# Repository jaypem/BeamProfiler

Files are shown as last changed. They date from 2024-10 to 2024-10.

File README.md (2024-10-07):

# BeamProfiler pd©

The BeamProfiler pd1© allows to measure laser beams with diameters up to 4 mm. It is controlled by a Raspberry Pi, a small single-board computer with an adapted 7” touch display.

| Camera parameter           | Laser beam                | BeamProfiler results              |
| -------------------------- | ------------------------- | --------------------------------- |
| Sensor Size: 5,7 x 4,28 mm | Beam diameter: up to 4 mm | Beam diameter $ \frac{1}{e^2} $ |
| Pixel: 2592 x 1944         | Wavelength: 350 – 950 nm | Width and height                  |
| Pixel Size: 2,2 x 2,2 µm  |                           | Image with scale                  |

For more information see also: `BeamProfiler-pd1_manual.pdf`

©Dirk Müller, JanPhilipp Praetorius

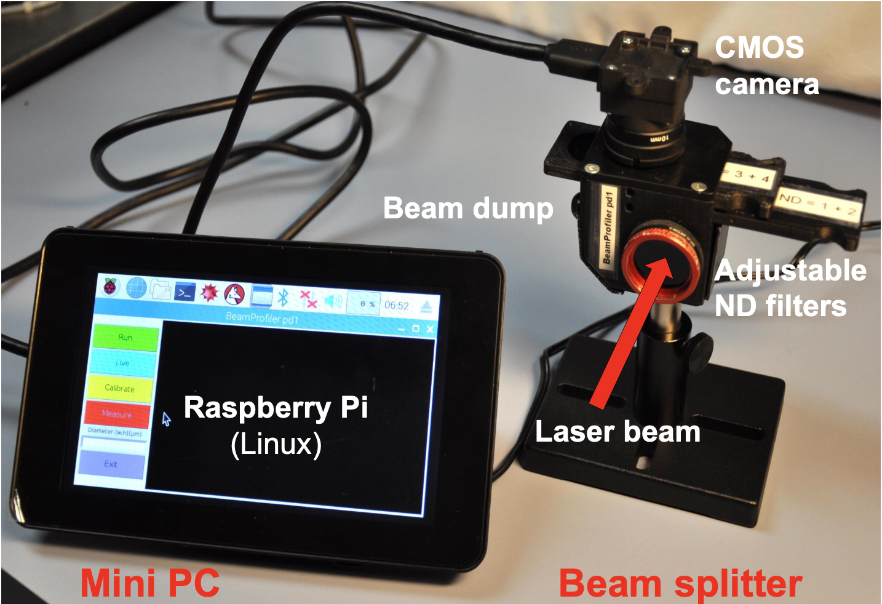
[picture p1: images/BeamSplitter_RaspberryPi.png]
BeamSplitter_RaspberryPi

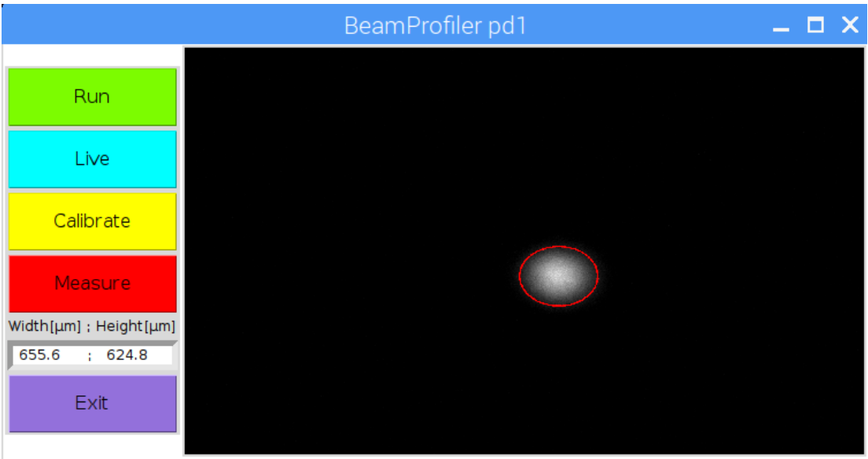
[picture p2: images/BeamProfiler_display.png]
BeamProfiler_display


## Assembly of the Raspberri Pi

### Install heat sinks one the Pi

[raspberrytips](https://raspberrytips.com/install-heat-sinks-raspberry-pi/)

### Setting up your Raspberry Pi

[https://projects.raspberrypi.org/en/projects/raspberry-pi-setting-up](https://projects.raspberrypi.org/en/projects/raspberry-pi-setting-up)

1. insert SD-card
2. connect the mouse to a USB-port
3. connect a keyboard to a USB-port
4. connect a screen via HDMI
5. connect power supply to micro-USB(the Pi starts to boot)

### Finish Setup

6. select corresponding settings

## Installation

### Install miniconda

run as bash command:

```bash
wget http://repo.continuum.io/miniconda/Miniconda-3.16.0-Linux-armv7l.sh
```

### Install python3 with

corresponding libraries on the Pi

7. [OpenCV]([https://tutorials-raspberrypi.de/opencv-auf-dem-raspberry-pi-installieren/](https://tutorials-raspberrypi.de/opencv-auf-dem-raspberry-pi-installieren/))

[fhttps://www.alatortsev.com/2018/09/05/installing-opencv-3-4-3-on-raspberry-pi-3-b/](https://www.alatortsev.com/2018/09/05/installing-opencv-3-4-3-on-raspberry-pi-3-b/)

OR

```bash
sudo apt install python3-opencv
```

Access via
ssh: [https://www.raspberrypi.org/documentation/remote-access/ssh/](https://www.raspberrypi.org/documentation/remote-access/ssh/)

8. install matplotlib

```bash
sudo pip3 install matplotlib
```

9. if numpy must be updated

```bash
sudo pip3 install –upgrade numpy
```

10. install PIL.ImageTk

```bash
sudo apt-get install python3-pil.imagetk
```

11. follow installation instruction for camera-library: [https://github.com/basler/pypylon](https://github.com/basler/pypylon)

11.1     download pylon-software for OperatingSystem: *ARM-32-bit:*

https://github.com/Basler/pypylon/releases:

install corresponding lib :

for python 3.5 install [pypylon-1.3.1-cp35-cp35m-linux_armv7l.whl](https://github.com/basler/pypylon/releases/download/1.3.1/pypylon-1.3.1-cp35-cp35m-linux_armv7l.whl)

```bash
pip3 install pypylon-1.3.1-cp35-cp35m-linux_armv7l.whl
```

11.2 To
commit permission for executing the shell script by double click go to desktop and type:

```bash
chmod u+x BeamProfiler.sh
```

## Connect Pi with Touchscreen

12. Remove screws of controller board at the backside of the display, put Pi on the appropriate screw socket and mount the Pi with the screws
13. Connect the cables from the controller board with the Pi as shown in the following link:

[https://maker-tutorials.com/raspberry-pi-touchscreen-installieren-und-anschliessen-tipps-tricks/](https://maker-tutorials.com/raspberry-pi-touchscreen-installieren-und-anschliessen-tipps-tricks/)

14. Start the Pi and if necessary rotate the display with the following command:

```bash
sudo nano / boot /config.txt
```

and add the following line on the top of the file:

`„lcd_rotate=2“`

15. Save the file and test the shell script **„BeamProfiler.sh“** on the Desktop

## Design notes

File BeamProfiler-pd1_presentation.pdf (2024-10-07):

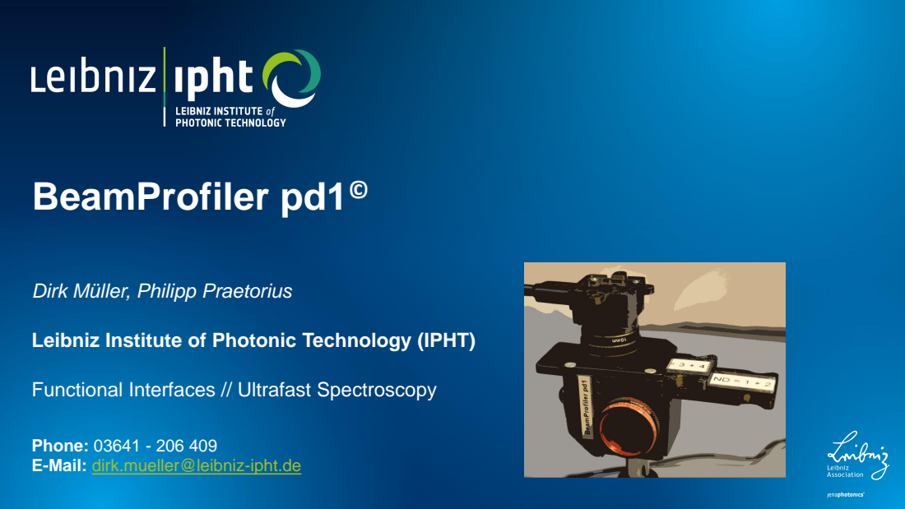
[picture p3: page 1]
BeamProfiler pd1©

Dirk Müller, Philipp Praetorius

Leibniz Institute of Photonic Technology (IPHT)

Functional Interfaces // Ultrafast Spectroscopy

Phone: 03641 - 206 409
E-Mail: dirk.mueller@leibniz-ipht.de

## Components of the BeamProfiler pd1©

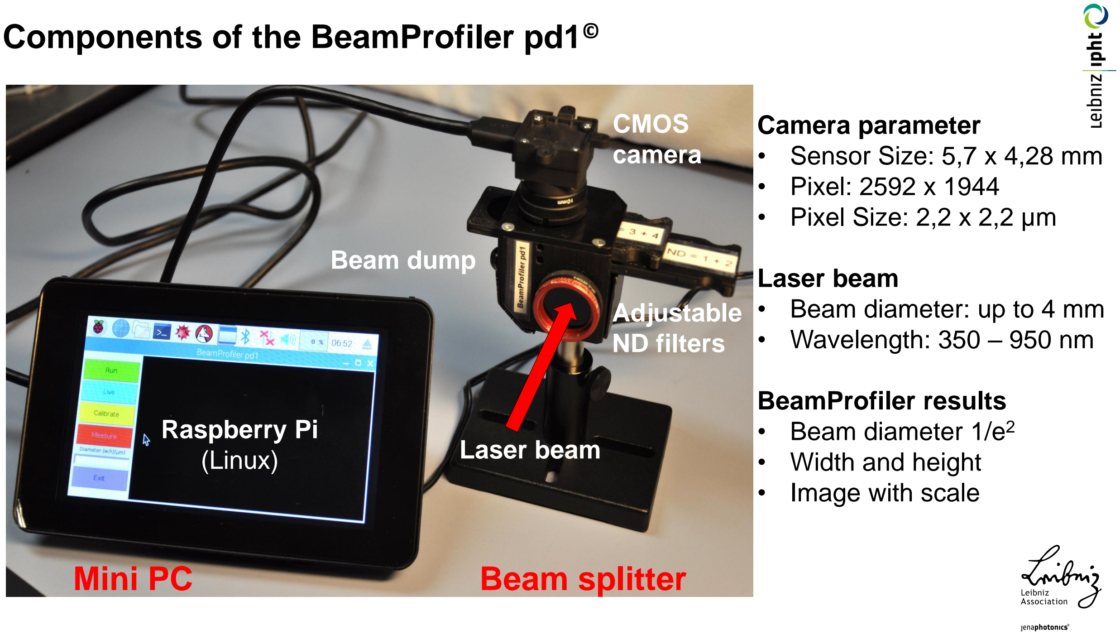
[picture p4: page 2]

CMOS
camera

Raspberry Pi
(Linux)

Beam dump

Laser beam

Adjustable
ND filters
Mini PC | Beam splitter

Camera parameter
- Sensor Size: 5,7 x 4,28 mm
- Pixel: 2592 x 1944
- Pixel Size: 2,2 x 2,2 µm

Laser beam
- Beam diameter: up to 4 mm
- Wavelength: 350 – 950 nm

BeamProfiler results
- Beam diameter 1/e

2
- Width and height
- Image with scale

## Setup of the BeamProfiler pd1©

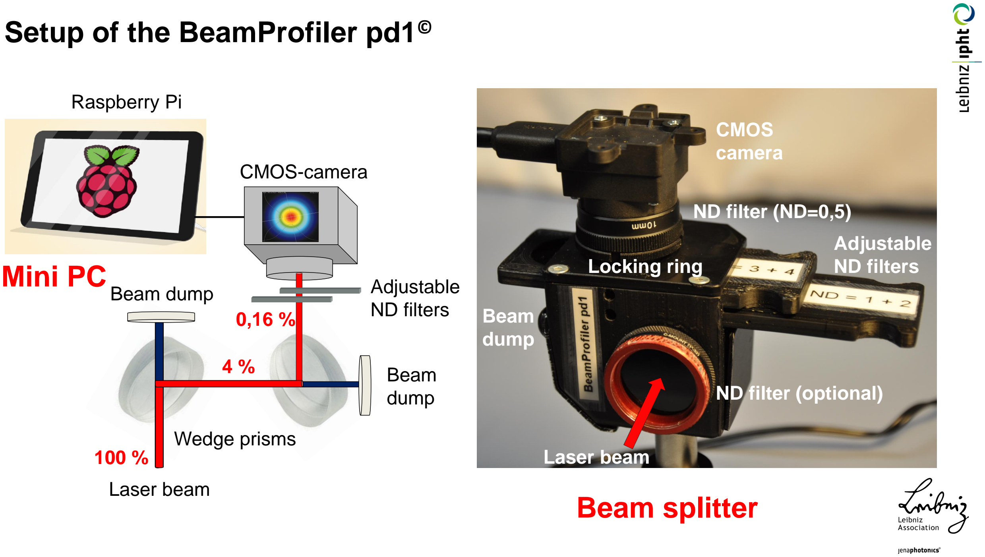
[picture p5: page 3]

CMOS-camera

Raspberry Pi

Adjustable
ND filters

Wedge prisms

Beam
dump

Beam dump

Laser beam

CMOS
camera

Beam
dump

Laser beam

Adjustable
ND filters

ND filter (ND=0,5)

Locking ring

ND filter (optional)

## Beam splitter

## Mini PC

100 %

4 %

0,16 %

## Adjustment of the BeamProfiler pd1©

Avoiding a damage of eyes and sensor
- Use the laser with the lowest power.
- Attenuate the laser power by external reducers (i.e. neutral density filter wheel).

Adjustment of the BeamProfiler pd1©
- Position the beam splitter at the right position. Consider the distance of about 88 mm from entrance to the sensor.
- Adjust the laser through the beam splitter primarily without the camera to find the weak signal behind the wedges.
- Turn off the camera together with the ND filter very carefully from the beam splitter.
- Put a white card or a diffusion disk on the exit of the beam splitter and adjust carefully the laser to the exit of the beam splitter. Pay attention to
the laser safety!
- Turn on the camera after adjusting the laser into

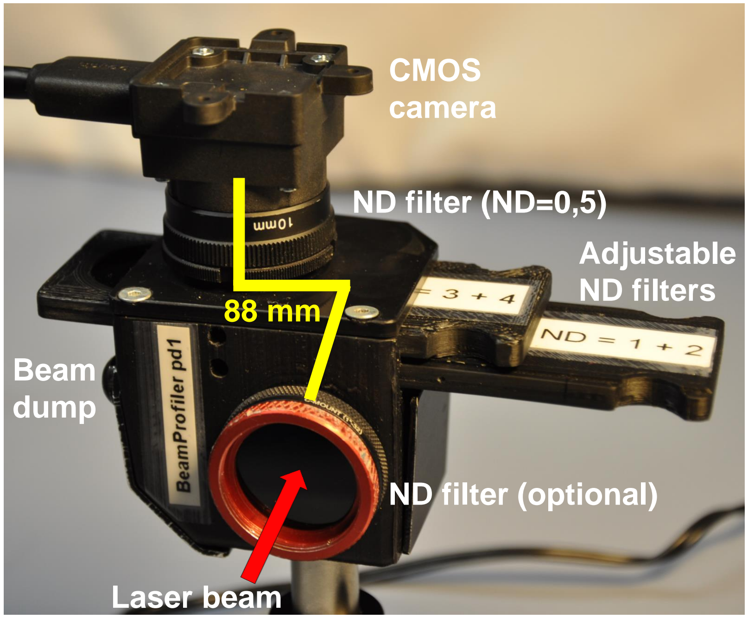
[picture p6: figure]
CMOS camera; Beam dump; Laser beam; Adjustable ND filters; ND filter (ND=0,5); ND filter (optional)

the center of the exit of the beam splitter. | Beam splitter

## Changing the direction of the BeamProfiler

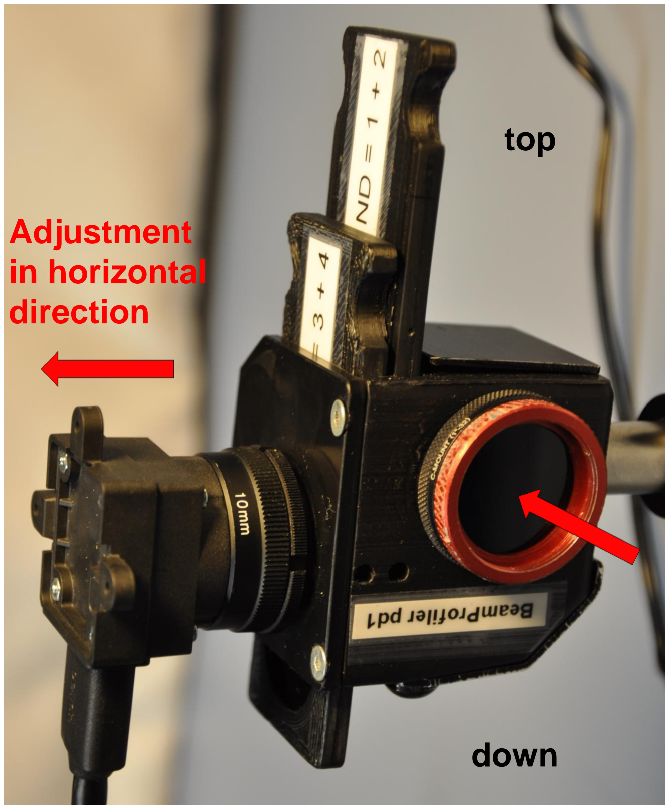
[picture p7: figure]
top; down; Adjustment in horizontal direction

## Operation of the BeamProfiler pd1©

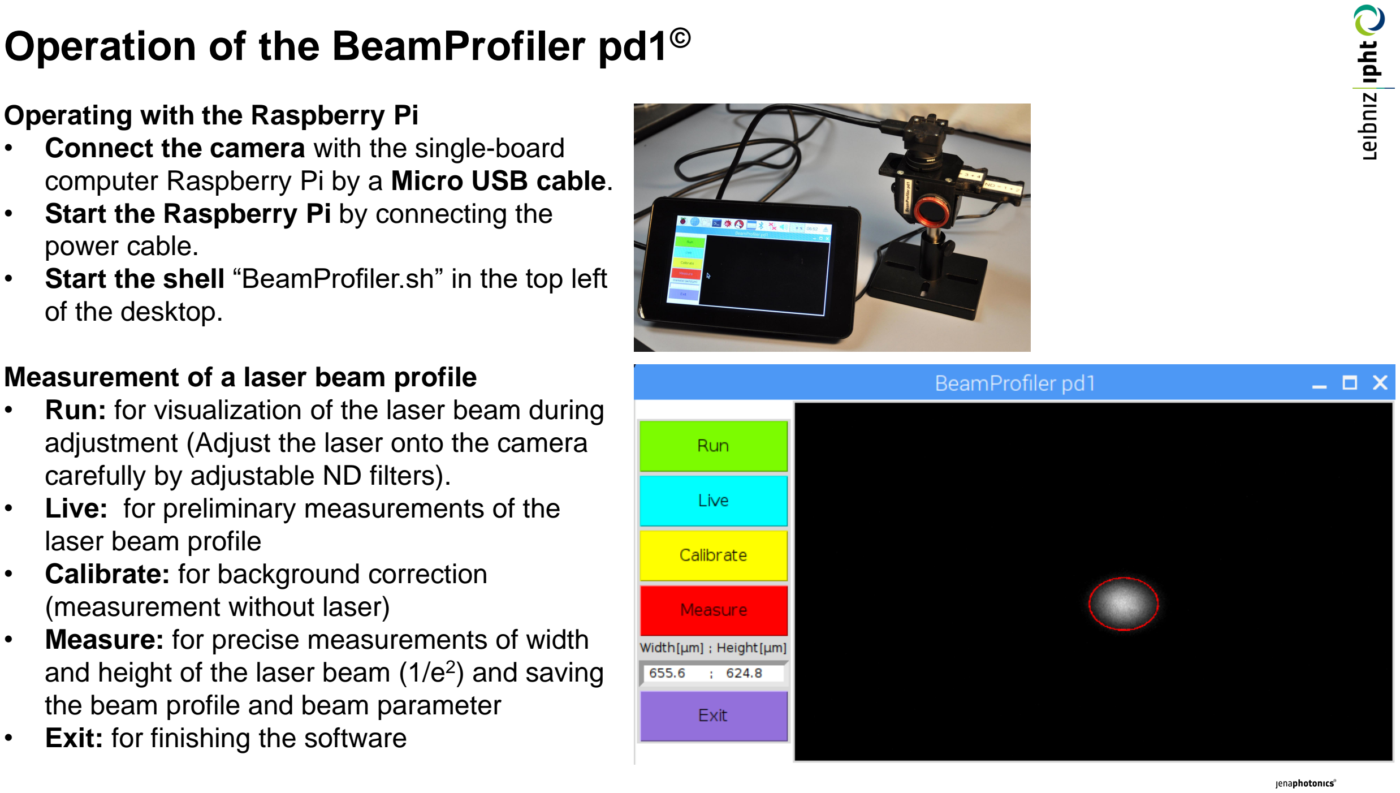
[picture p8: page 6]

Operating with the Raspberry Pi
- Connect the camera with the single-board computer Raspberry Pi by a Micro USB cable.
- Start the Raspberry Pi by connecting the power cable.
- Start the shell “BeamProfiler.sh” in the top left of the desktop.

Measurement of a laser beam profile
- Run: for visualization of the laser beam during adjustment (Adjust the laser onto the camera carefully by adjustable ND filters).
- Live: for preliminary measurements of the laser beam profile
- Calibrate: for background correction (measurement without laser)
- Measure: for precise measurements of width and height of the laser beam (1/e²
) and saving
the beam profile and beam parameter
- Exit: for finishing the software

## Output of the image and the measurement result

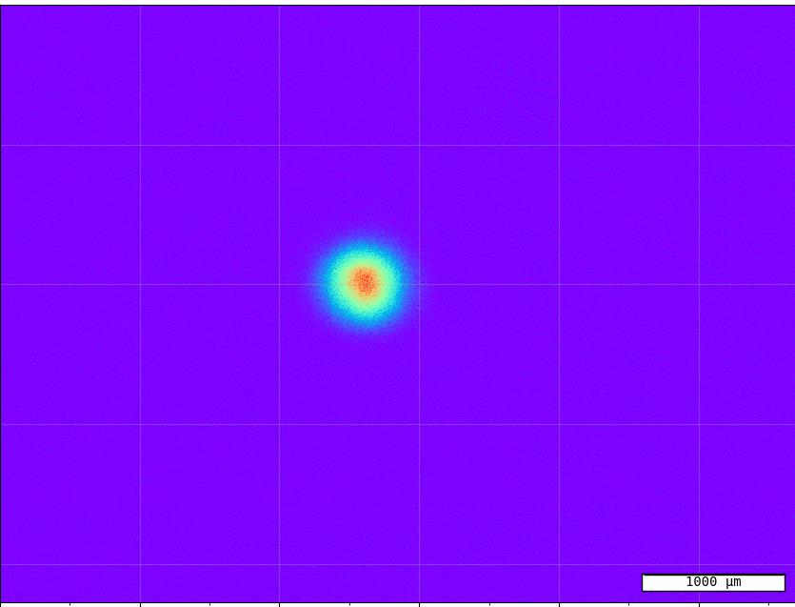
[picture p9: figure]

Beam paramter
- Beam diameter 1/e

2
- Width and height in µm

## Directory structure of the Raspberry Pi

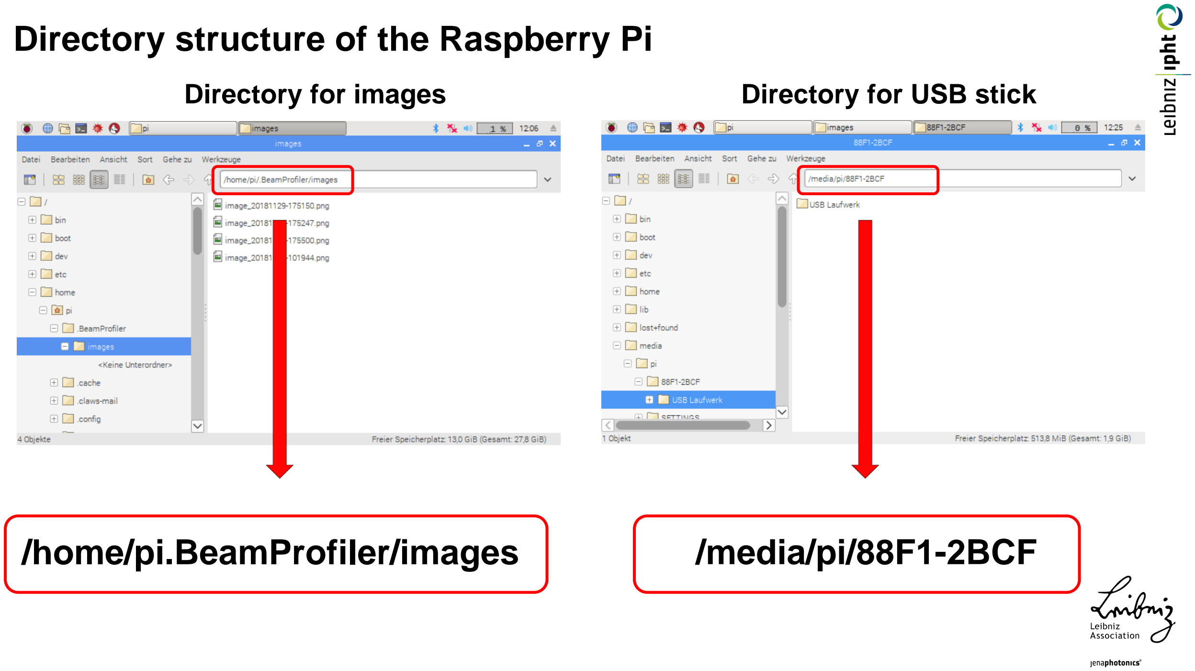
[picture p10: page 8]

Directory for images | Directory for USB stick
/home/pi.BeamProfiler/images | /media/pi/88F1-2BCF

## Examples: beam profile of a laser pointer

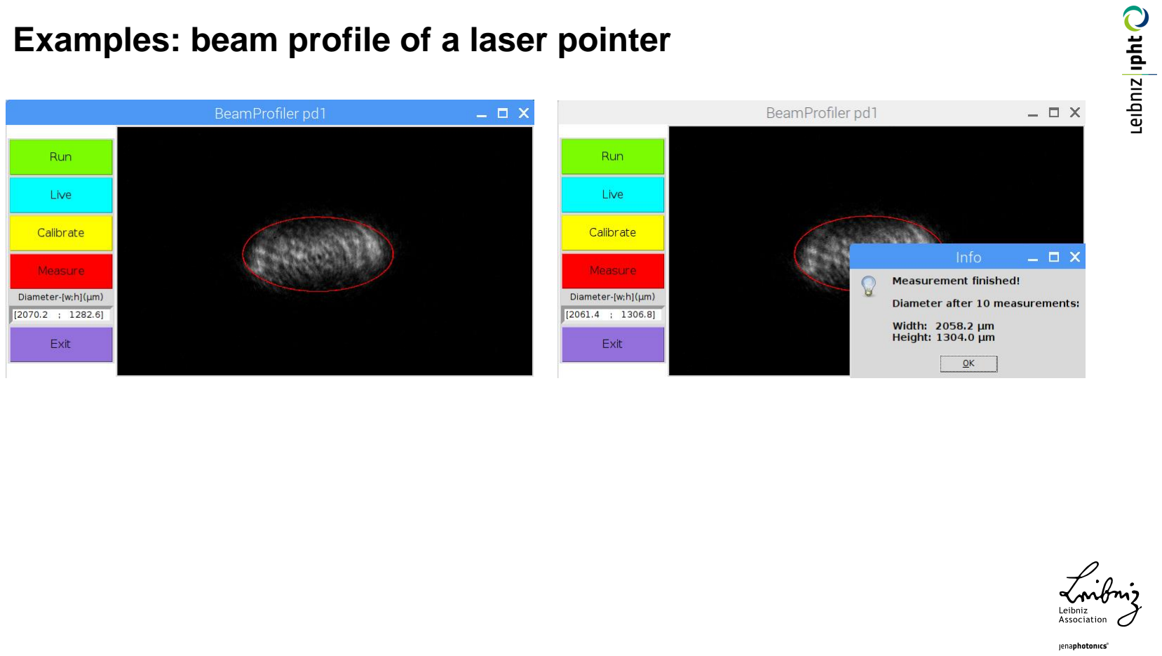
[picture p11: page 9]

## Examples: beam profile of the Tsunami laser (S21, streak camera)

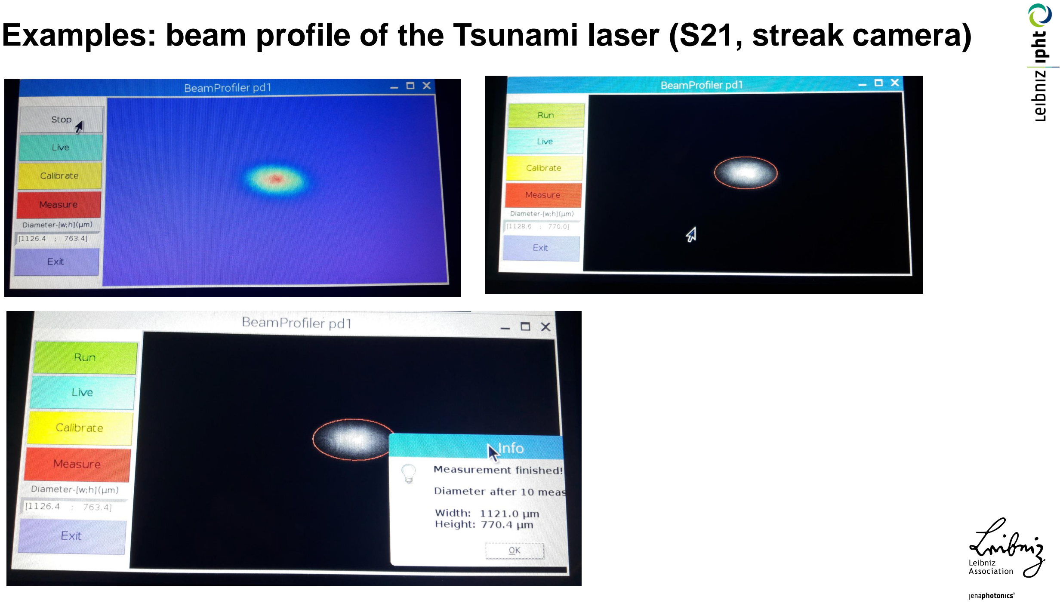
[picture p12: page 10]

## Examples: beam profile of the Legend (191.1, TA)

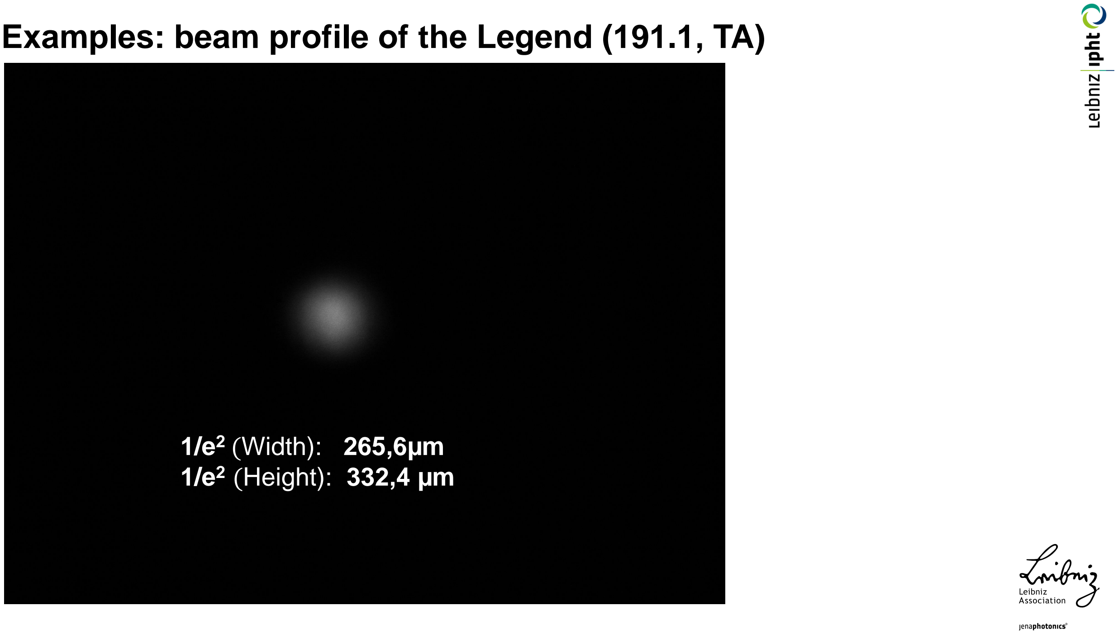
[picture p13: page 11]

1/e²
(Width): 265,6µm
1/e² (Height): 332,4 µm

## Comparison with commercial BeamProfiler (laser diode, LTG 218)

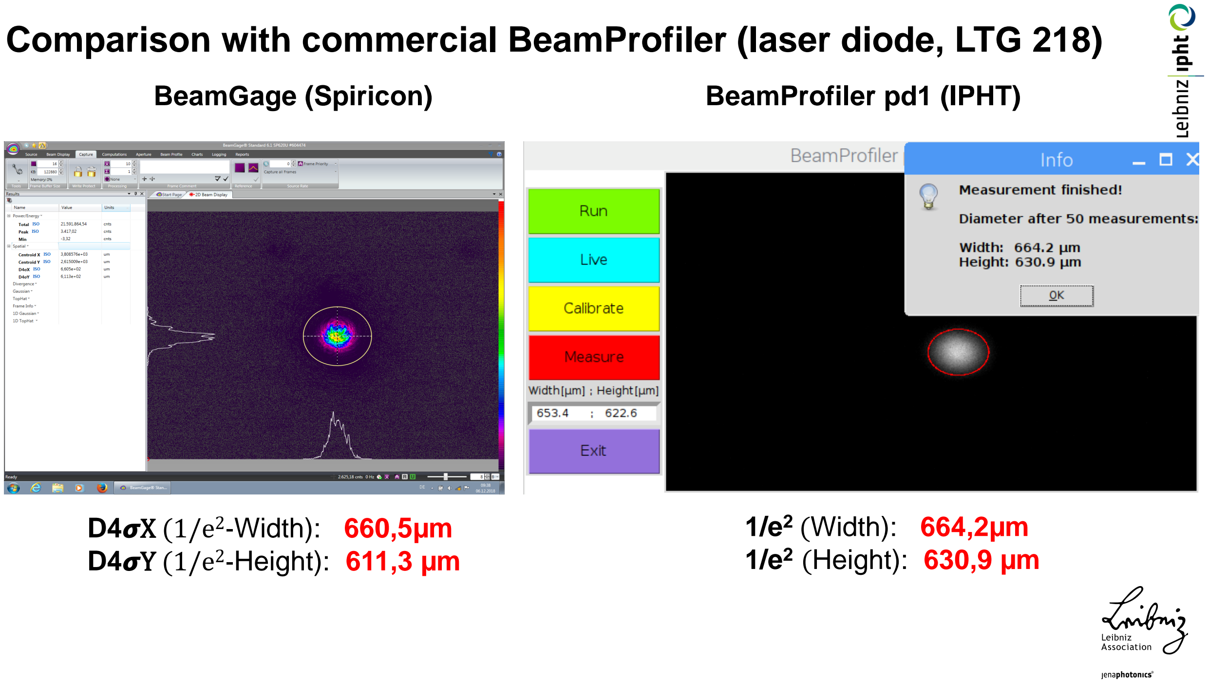
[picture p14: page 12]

BeamGage (Spiricon) | BeamProfiler pd1 (IPHT)

### D4σX (1/e²

-Width): 660,5µm

### D4σY (1/e²

-Height): 611,3 µm

1/e²
(Width): 664,2µm
1/e² (Height): 630,9 µm

## BeamProfiler pd1© - Questions?

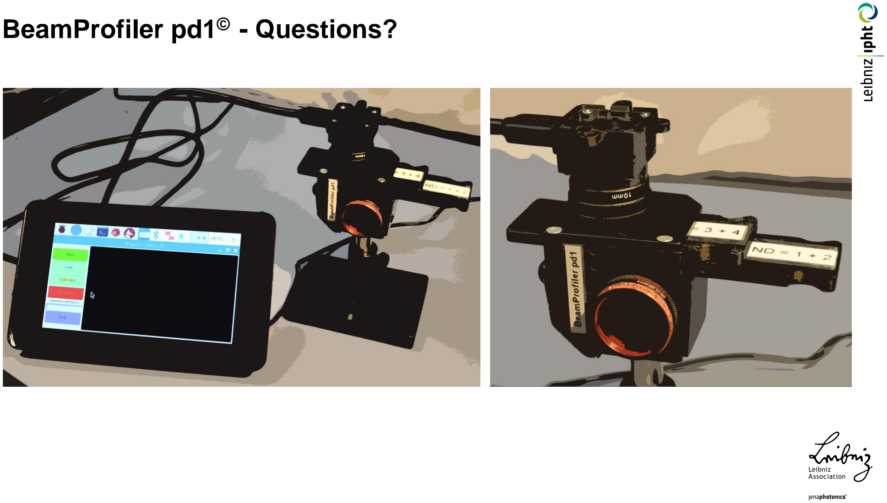
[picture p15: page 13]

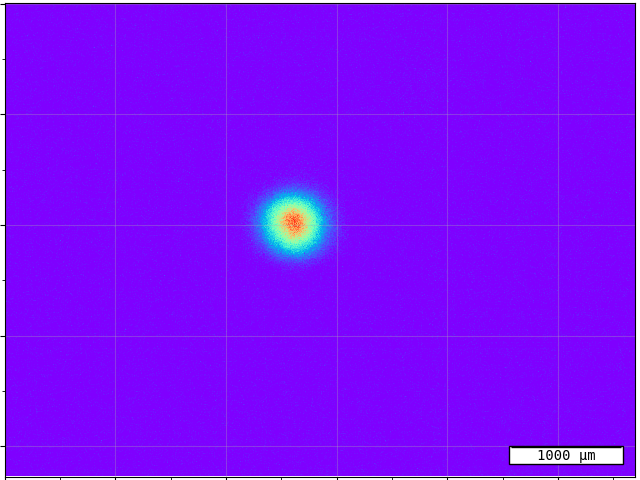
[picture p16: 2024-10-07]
images/hallo.png

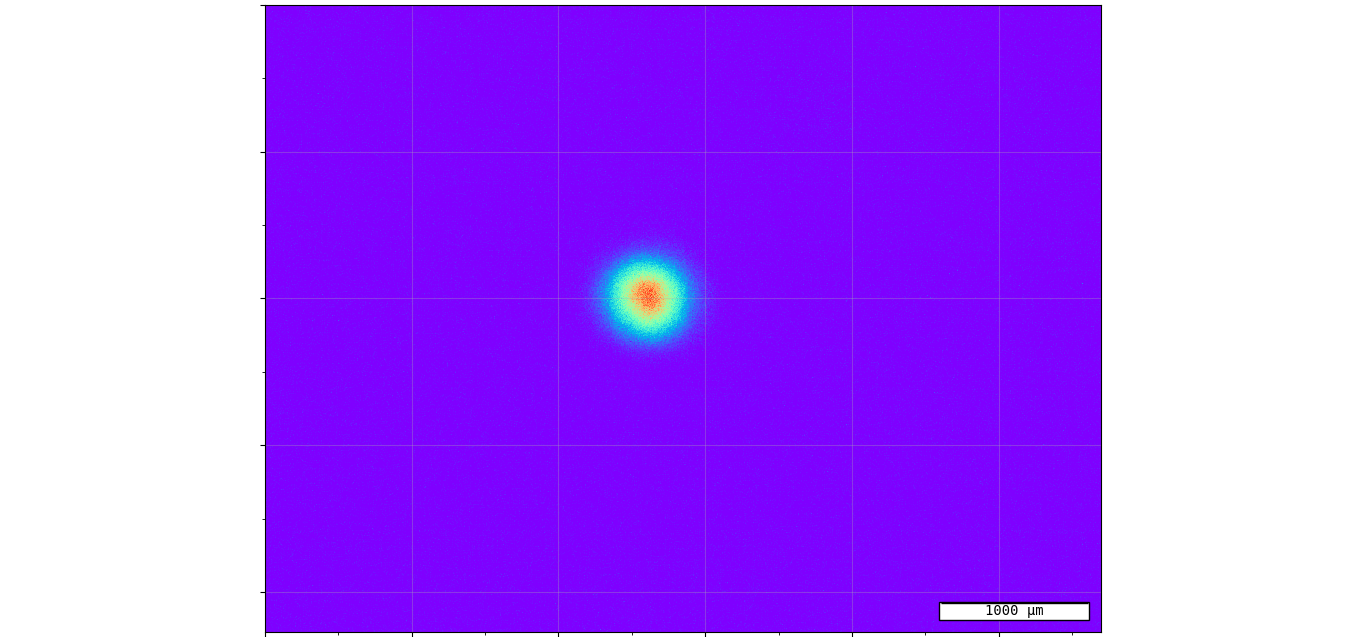
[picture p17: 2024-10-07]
images/figure_1.png

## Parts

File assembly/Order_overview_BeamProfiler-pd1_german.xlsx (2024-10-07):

Beam Profiler pd1
 |  |  |  |  |  | 2019-02-07
Komponente | Bezeichnung | Hersteller | Parameter | Preis/€ | Anzahl | Preis/€
Strahlteiler Mechanik
Grundkörper | Druckmaterial | Heintzmann | siehe Zeichnung |  | 1
Filterhalterung (2x) | Druckmaterial | Heintzmann | siehe Zeichnung |  | 2
Adapter Kamera | C-Mount Adapter | Werkstatt | siehe Zeichnung |  | 1
Strahlfalle | Beam Block | Werkstatt | siehe Zeichnung |  | 2
Strahlteiler Optik
ND Halterung | CML05 Adapter | Thorlabs | C-Mount, 5 mm Länge | 15.82 | 1 | 15.82
Retaining Ring | CMRR | Thorlabs | C-Mount | 11.18 | 1 | 11.18
Konterring | CMNT1-C-Mount Locking Ring | Thorlabs | C-Mount, 1,25" Außendurchmesser | 9.46 | 1 | 9.46
Keilplatten | PS812-01" Round Wedge Prism | Thorlabs | Winkel: 6° | 31.29 | 2 | 62.58
ND Filter | NE05B, NE20B, etc. | Thorlabs | 25 mm, OD: 0.5,1,2,3,4; einschiebbar | 30.37 | 5 | 151.85
Kamera
Kamera (Basler) | daA2500-14um CS | Rauscher | 2590x1942, 2,2µm/5,7x4,2mm/360-1030nm | 149.00 | 1 | 149.00
Kameragehäuse | BAS-ACC-VAR-2200000164 | Rauscher | dart mounting cover | 5.80 | 1 | 5.80
Kamerakabel | USB 3.0 Micro-B Kabel | Rauscher ? |  | ?? | 1
Rechner
PC, Monitor | RASP 3 BDL 7TD (Amazon) | Reichelt | Pi3, 7"Display, Gehäuse, Netzteil, 16GB | 169.94 | 1 | 169.94
Gesamt netto |  |  |  |  |  | 575.63
Gesamt brutto |  |  |  |  |  | 685.00

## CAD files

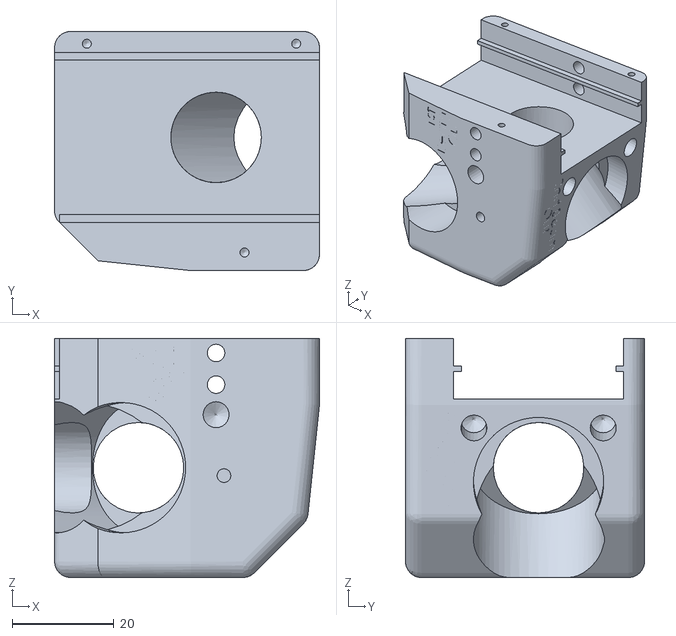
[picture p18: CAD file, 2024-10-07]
assembly/BeamSplitter_base-body/BeamSplitter_Grundkörper.stl
52.1 x 47.0 x 47.0

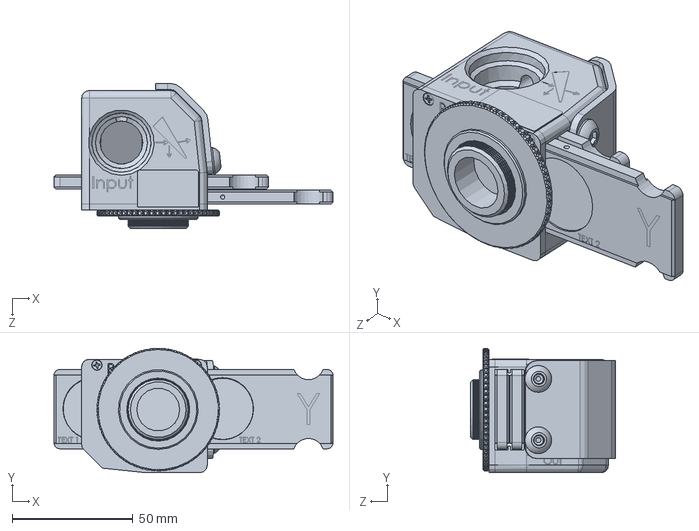
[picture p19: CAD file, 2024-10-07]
assembly/BeamSplitter_base-body/LBS-300s.SLDPRT
115.6 x 51.6 x 60.1 mm

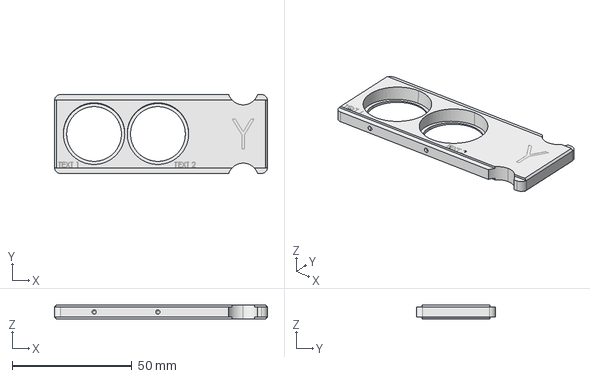
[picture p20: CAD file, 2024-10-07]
assembly/BeamSplitter_base-body/ND_Filterhalterung.fcstd
88.9 x 33.0 x 5.72 mm

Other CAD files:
assembly/BeamSplitter_base-body/BeamProfiler_Grundkörper.fcstd
assembly/BeamSplitter_base-body/LBS-300s.DXF
assembly/BeamSplitter_base-body/LBS-300s.stl
assembly/BeamSplitter_base-body/ND_Filterhalterung.stl

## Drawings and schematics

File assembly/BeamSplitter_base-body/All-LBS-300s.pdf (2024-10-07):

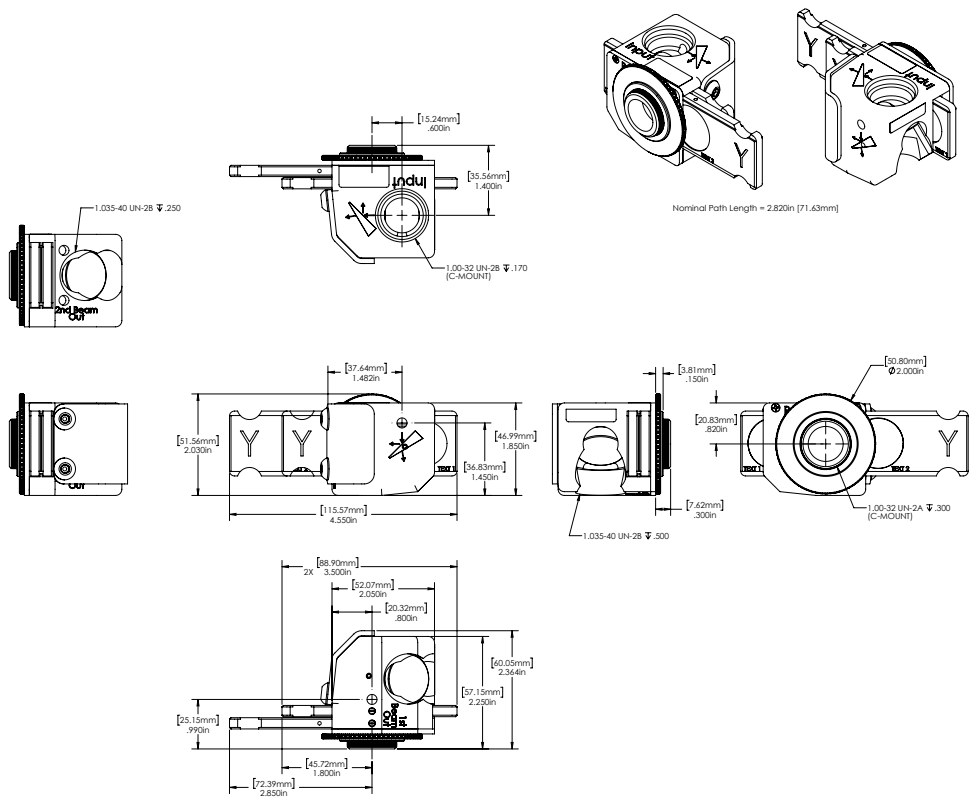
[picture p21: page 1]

Nominal Path Length = 2.820in [71.63mm]

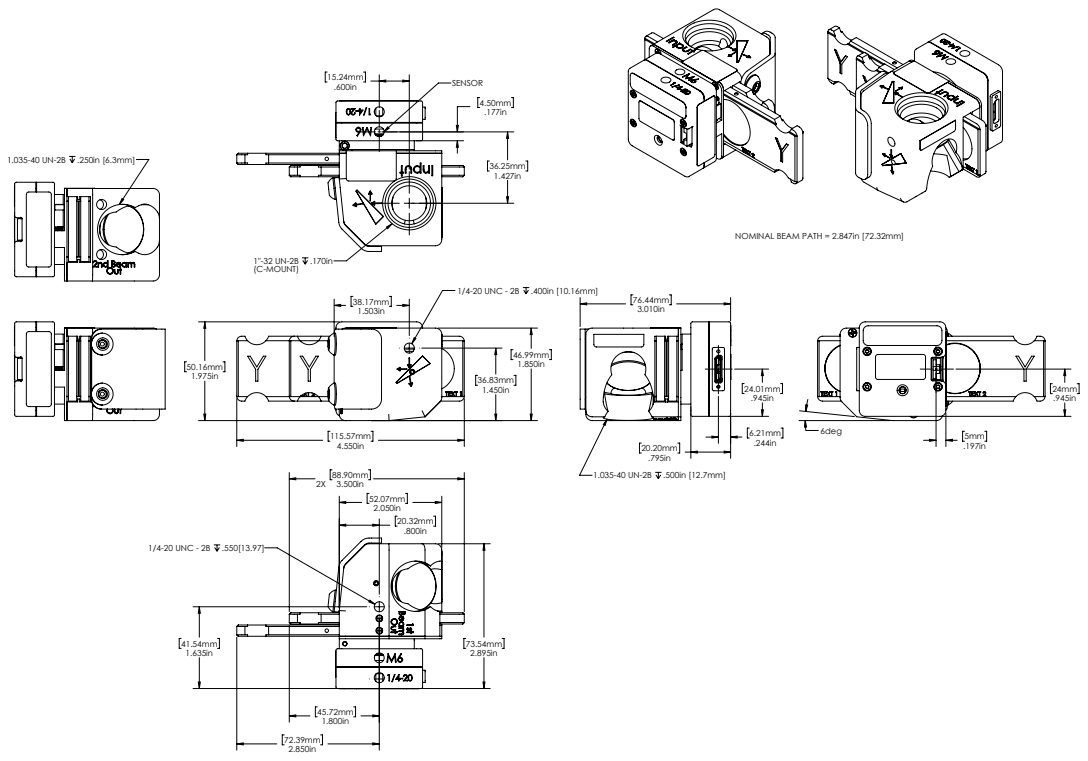
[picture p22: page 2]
1/4-20 UNC - 2B .400in [10.16mm]; 1/4-20 UNC - 2B .550[13.97]

NOMINAL BEAM PATH = 2.847in [72.32mm]

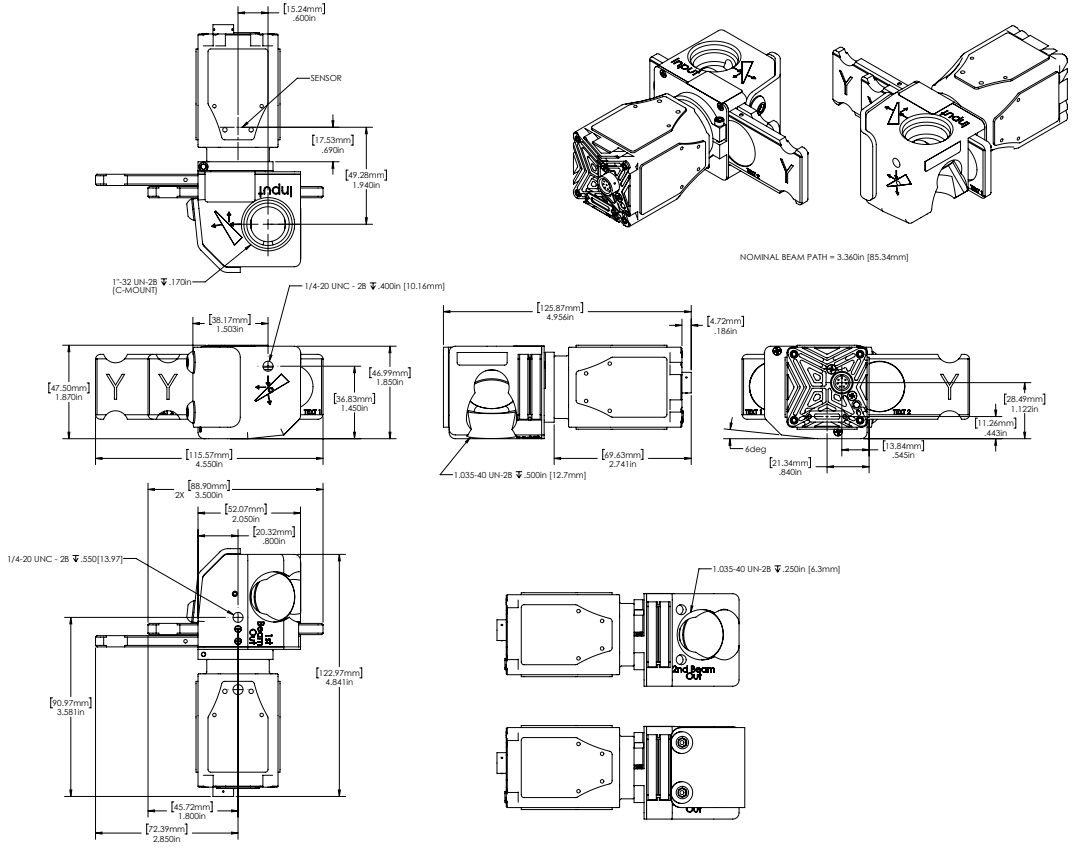
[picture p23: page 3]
1/4-20 UNC - 2B .400in [10.16mm]; 1/4-20 UNC - 2B .550[13.97]

NOMINAL BEAM PATH = 3.360in [85.34mm]

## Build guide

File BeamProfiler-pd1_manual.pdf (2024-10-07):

# BeamProfiler pd1©

# Manual

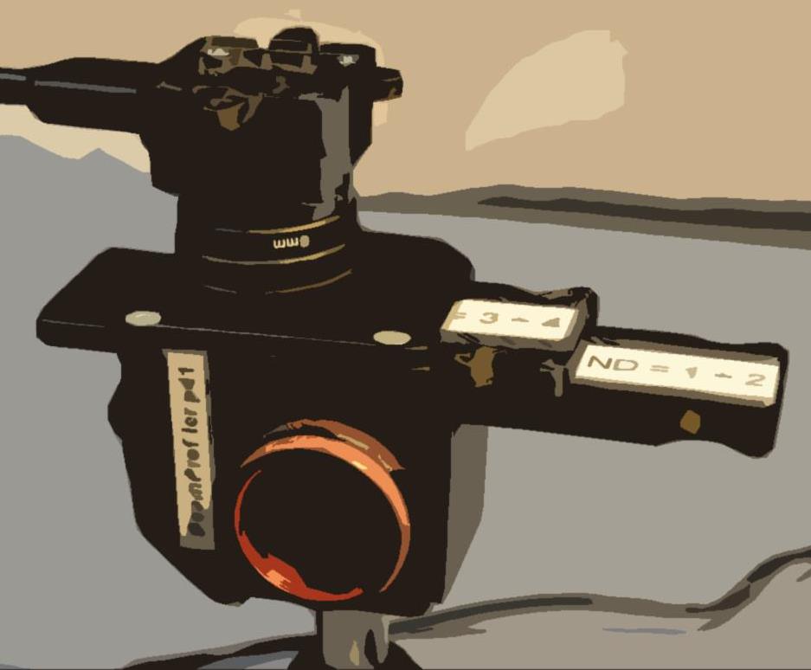
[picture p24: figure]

## Dirk Müller, Jan-Philipp Praetorius

## Leibniz Institute for Photonic Technology

Functional Interfaces / Ultrafast Spectroscopy

## December 2018

SETUP of the BeamProfiler pd1©

The BeamProfiler pd1©
allows to measure laser beams with diameters up to 4 mm. It is

controlled by a Raspberry Pi, a small single-board computer with an adapted 7” touch

display (Fig. 1). With the help of a self developed software it is possible to visualize and measure the 1/e² diameter (width and height) of laser beams.

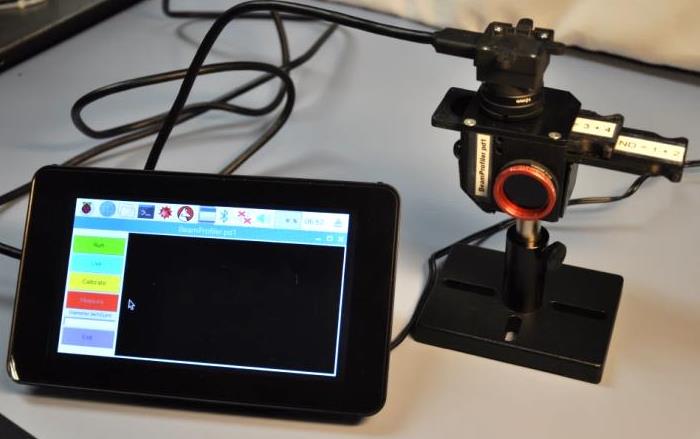
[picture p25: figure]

Fig. 1: BeamProfiler pd1©
connected to a small single-board computer Raspberry Pi

The beam splitter is designed so that the preferential polarization selection effect of a single

wedge is cancelled out and the resulting beam image is polarization corrected to restore the

polarization components of the original beam. The beam splitter operates by reflecting the

incoming beam from the front surface of a pair of wedge prisms through 90 degrees into the

camera (Fig. 2). Approximately 99 % of the beam is transmitted through the beam splitter

with 0,01 % passed on to the camera. A set of adjustable ND filters (ND = 1, 2, 3, 4)

performed as slides are provided to make final intensity adjustments to the beam before it

reaches the camera sensor.

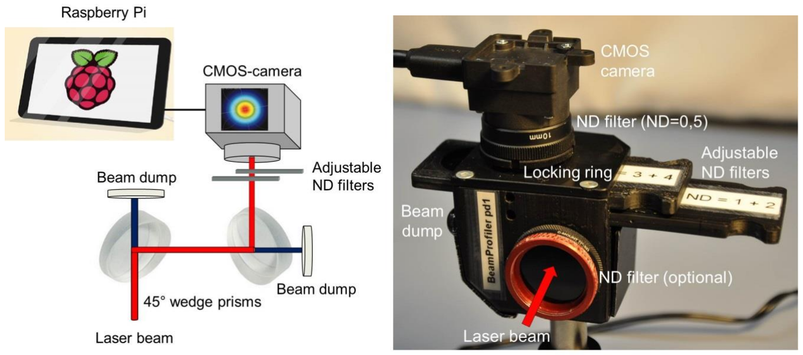
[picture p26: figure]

Fig. 2: Setup of the beam splitter

OPERATION of the BeamProfiler pd1©

### 1. Avoiding a damage of the camera sensor

- The sensor of the BeamProfiler pd1©
is very sensitive and the danger of a damage is very

high. That’s why the measurements should do very carefully especially when the laser

has to be measured in the focus of a lens.

- To avoid a damage of the sensor the laser has to attenuate to a suitable range. The main

part of the beam power is transmitting the pair of wedge prisms and is so absorbed by

two beam dumps. Furthermore one ND filter with ND = 0,5 is permanent attached in

front of the camera entrance. For very low signal it can be removed. The other ND filters

with ND = 1, 2, 3, 4 can be used as slides optional in front of the camera.

### 2. Adjustment of the BeamProfiler pd1©

- If you want to measure the laser beam profile at a special position (i.e. in the focus), you

have to consider the distance between the entrance of the beam splitter until the sensor

of the camera. The distance from the entrance of the beam splitter until the sensor is about 88 mm. So you have to put the BeamProfiler pd1©
88 mm before the position

where you want to measure the beam profile.

- It is recommended to adjust the laser through the beam splitter primarily without

camera to find the weak signal behind the wedges. For that hold on the locking ring and

turn off the camera together with the locking ring carefully from the beam splitter. Put a

white card or a diffusion disk onto the exit of the beam splitter instead of the camera

and adjust the beam splitter (with attention to the laser safety!) until you see the laser

beam in the center of the beam splitter exit.

### 3. Operating the BeamProfiler pd1©with the Raspberry Pi

- Connect the camera with the single-board computer Raspberry Pi by a Micro USB cable.
- The Raspberry Pi has no power switch. That’s why you have to connect the power cable

and the Raspberry Pi will start up.

- Start the shell “BeamProfiler.sh” in the top left of the desktop and press Ausführen to

start the software.

### 4. Measurement of a laser beam profile

- RUN: For visualization of the laser beam press the RUN button (Fig. 3). Adjust the laser

with lowest power and start with maximum attenuation by ND filters to avoid a damage

of the camera sensor. With the ND filter slides make final intensity adjustments to the

beam for a good signal modulation and dynamic range.

- LIVE & MEASURE: For preliminary measurements press the LIVE button. The software

will measure the beam profile in a live mode. Only one image will be used to calculate the beam profile. In the software output you will get the 1/e²
- width and the height of
the laser beam. At the position of the 1/e²
decrease of the laser intensity there will be

signed a circle or an ellipse in the laser beam profile.

- CALIBRATE: For precise measurements previously a background correction is necessary.

For that reason switch off or block the laser and press the CALIBRATE button. The

software asks for the desired number of measurements. These number of background

images are accumulated to correct the following precise measurements.

- MEASURE: For precise measurements press the MEASURE button. The software

accumulates the desired number of images. After finishing there will be an output with the calculated 1/e² diameter (stated in width and height) of the laser beam. There is also

the possibility to save the image with the beam profile. The images are saved in

“/home/pi/.BeamProfiler/images/image_’date+time’” on the Raspberry Pi. You should

know the Raspberry Pi has not a battery buffered clock. That’s why date and time are not

correct in the filename. To copy the images on your USB stick you find the USB device

under the following directory: “/media/pi/88F1-2BCF”

- EXIT: For finishing the BeamProfiler software press the EXIT button. To shut down the

Raspberry Pi press Shutdown under the raspberry drop down menu at the top left.

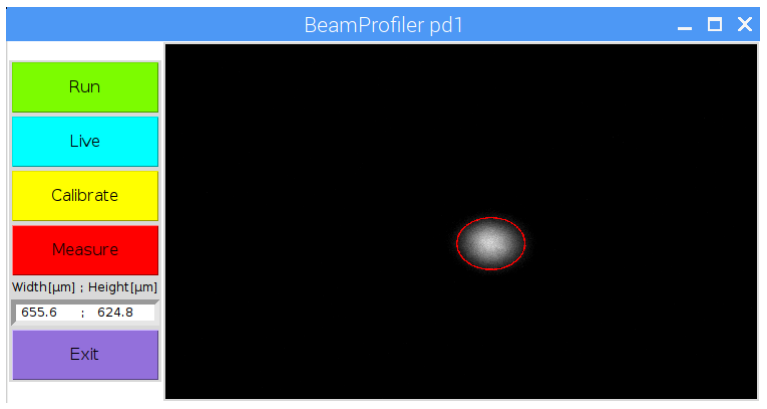
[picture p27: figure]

Fig. 3: Software of the BeamProfiler pd1
